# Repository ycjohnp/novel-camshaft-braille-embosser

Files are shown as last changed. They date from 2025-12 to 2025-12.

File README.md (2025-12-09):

# A Quieter and More Efficient Camshaft-Powered Braille Embosser 

**Introduction:**\
This project explores a camshaft-based approach to enhance braille embossers, addressing the challenges faced by visually impaired individuals. Traditional braille embossers are costly and noisy, hindering personal use. The proposed solution employs a camshaft system to improve efficiency, reduce noise, and lower costs. Unlike commercial alternatives ($2000-$5000) that require sound dampening, this camshaft-powered embosser operates quietly and is economically accessible at around 1000 RMB (approximately $160). The experiments conducted demonstrate the viability of this design, showcasing its potential as an affordable and effective braille embossing solution.

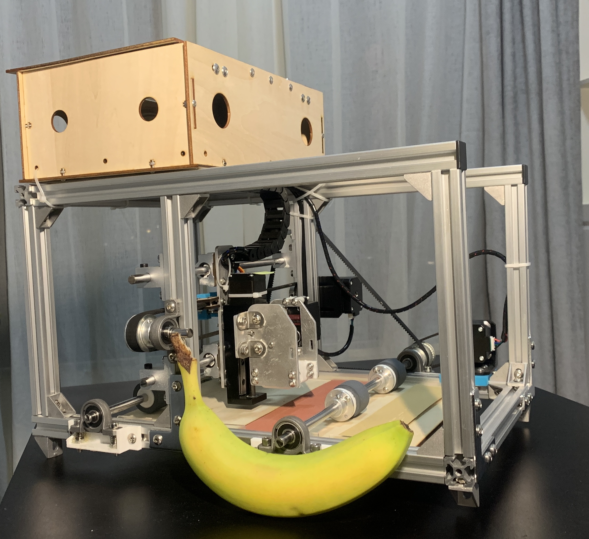
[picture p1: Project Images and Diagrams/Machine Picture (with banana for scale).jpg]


## Background

There are an estimated 43 million blind individuals worldwide, 233 million that are living with moderate to severe visual impairment.Visually impaired individuals rely on the use of braille letters instead of alphanumeric letters to write and read. Braille Characters are composed of a 2*3 grid of raised dots to form characters and can be generated through refreshable braille displays, manual braille writing slates, or braille embossers. Braille embossers are used to produce large amount of permanent braille characters.

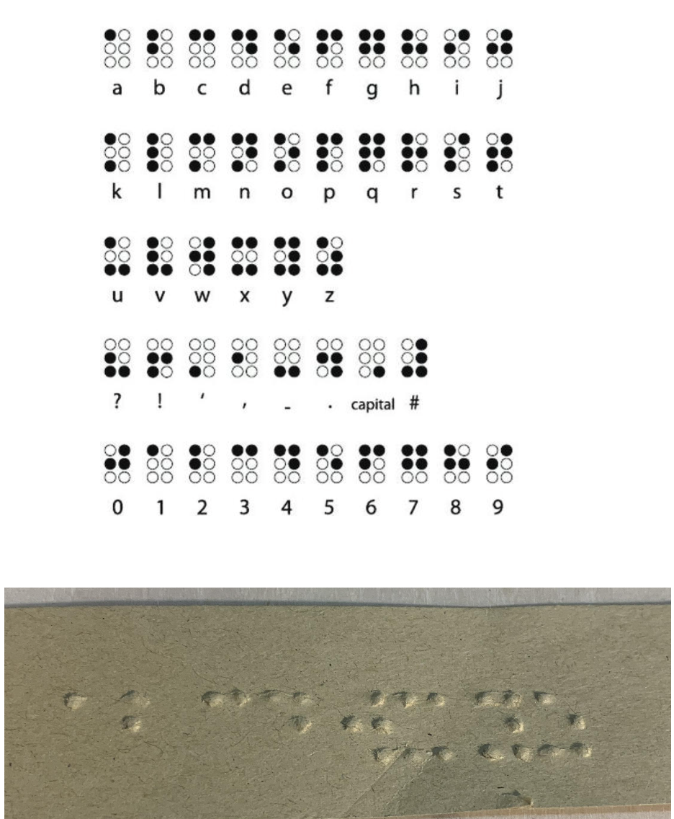
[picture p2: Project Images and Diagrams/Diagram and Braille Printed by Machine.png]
\
Diagram of braille characters and sample printed text from machine[^1].

Only 10% of blind individuals in the United States are proficient in braille. [^2] Commercial braille embossers, priced between $2000 and $5000, are impractical for personal use, mostly confined to schools and libraries. The widespread availability of such facilities has been limited, especially during the global pandemic. Currently, common commercial machines utilize loud linear solenoids, often necessitating sound dampening boxes. There is an absence of an efficient and quiet braille embosser suitable for home use in the current landscape.

**Engineering Goals:**\
Goal: Develop a highly efficient and low-noise braille embosser.
Design Criteria:
- Utilize off-the-shelf components.
- Generate braille following recognized standards.
- Enable simultaneous printing of multiple dots with scalability.
- Maintain operation noise below 60 dB.
- At a size for easy portability.
## Engineering Design

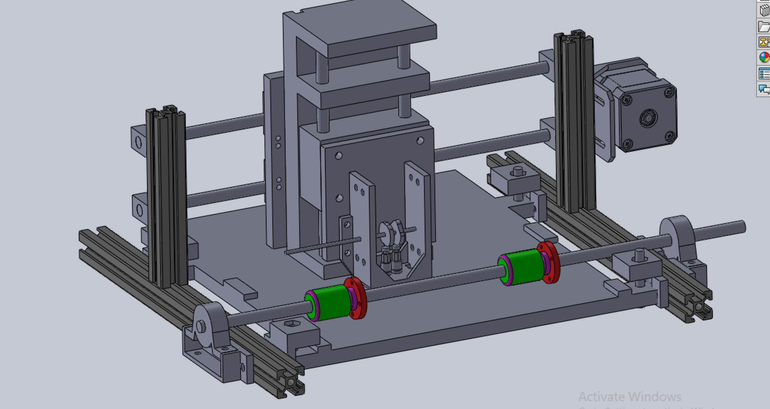
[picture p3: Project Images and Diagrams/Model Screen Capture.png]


This machine is based on a 3 axis motion system. 
In the diagram below: 
- The X axis is the belted linear motion system moves the printhead left and right on the as the machine is printing
- The Y axis is comprised of a system of rollers, that first feeds paper in, slides the paper up as each line of braille dots finishes printing, and releases the paper
- The Z axis is responsible for the up-down movement of the printhead. The lead-screw linear motion platform, pushes the printhead (and the print pins) into the paper, allowing for the dots to take shape

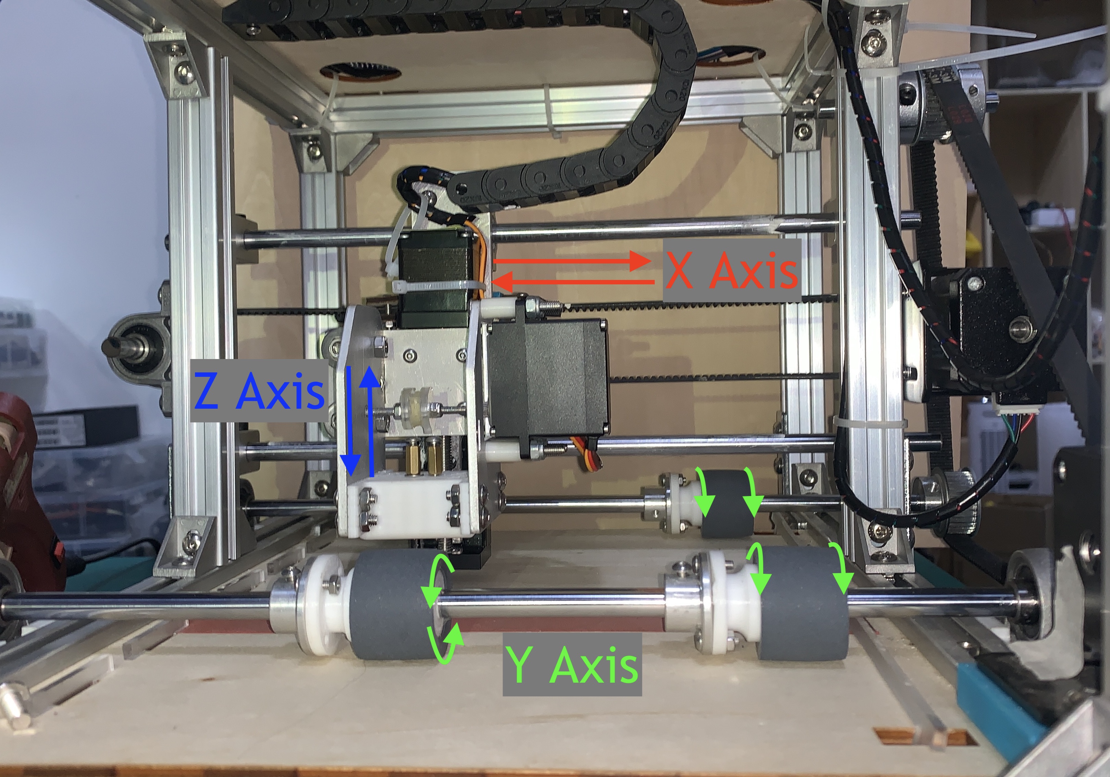
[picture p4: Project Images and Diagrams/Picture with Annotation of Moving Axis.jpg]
 

**Printhead Design:**

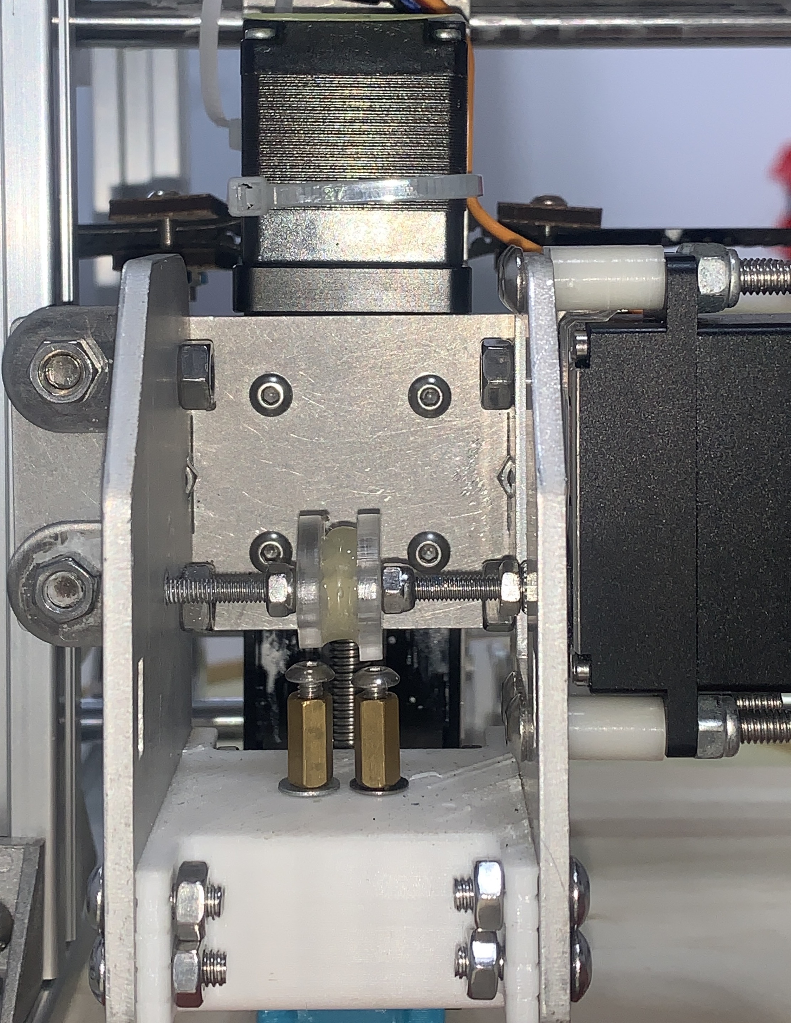
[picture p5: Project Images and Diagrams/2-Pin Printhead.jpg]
 

The main printhead assembly consists of a 360 degree servo that is a connected to a camshaft. This cam shaft has 2 cams on it and the cams have all the possible positions so that the print pins can pin all the possible combinations of "dot" and "no-dot". Underneath the cams are 2 print pins that are responsible for pushing the dots into the paper. These print pins are directly under the cams.

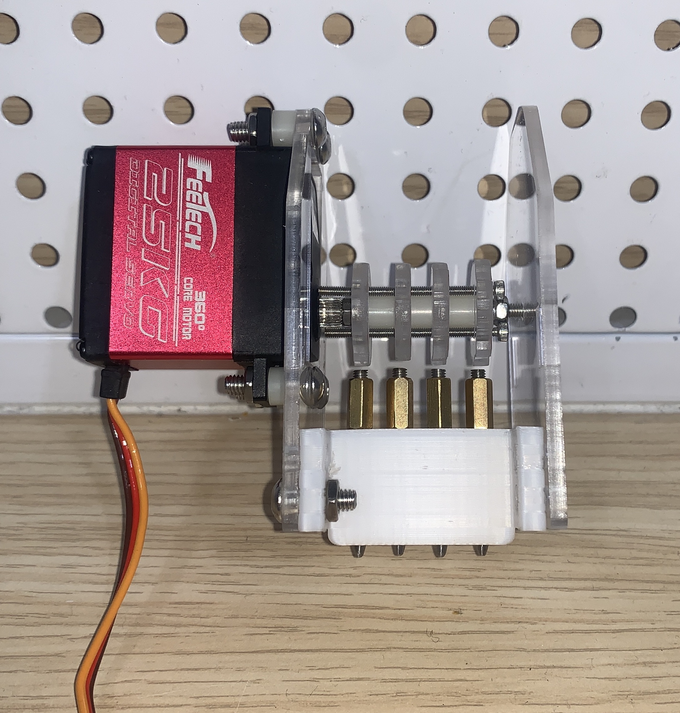
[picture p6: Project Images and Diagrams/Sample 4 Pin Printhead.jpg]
 

This 4 pin demo printhead shows theoretical maximum number of pins-per-printhead while maintaining accuracy when adjusting the positions of the cams. The protruding print pins are shown below.

## Testing

Several tests were conducted to verify the overall effectiveness of the printed braille. 

**Braille Dot Height Testing:**\
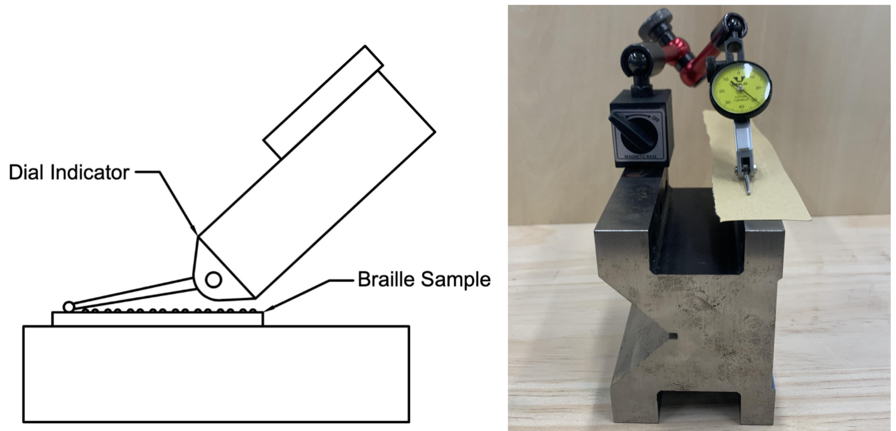
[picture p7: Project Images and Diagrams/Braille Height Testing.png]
 

From testing 5 different samples of the printed braille dots (characters: "abcdwxyz"), the average dot height was measured to be 0.32mm with a tolerance of ±0.12mm.

**Braille Dot Durability Testing:**

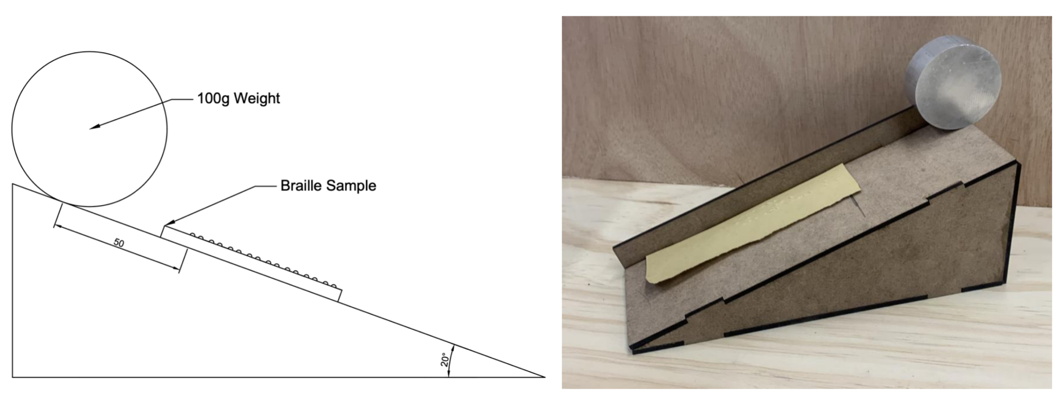
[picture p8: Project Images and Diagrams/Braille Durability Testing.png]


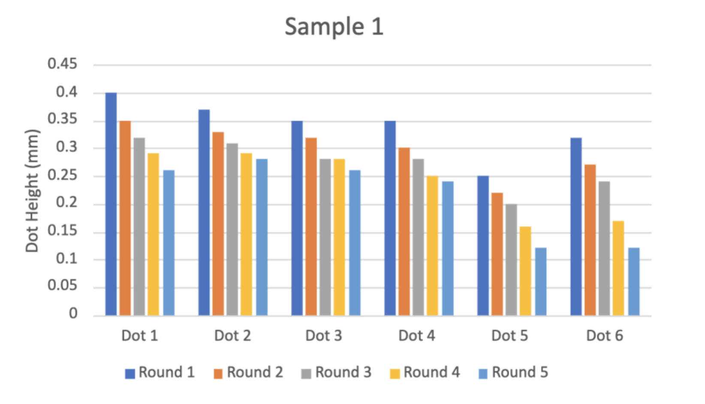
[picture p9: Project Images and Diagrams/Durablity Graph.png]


After 4 trials of durability testing, the average height loss for each dot was around 0.028mm.

## Conclusions

This project has showcased the feasibility of a low-cost,  efficient braille embosser employing a camshaft-based design. The printing mechanism has demonstrated success in generating braille dots and can be readily scaled to accommodate higher quantities. Future will be made particularly in areas such as exploring alternative manufacturing methods for print pins, elevating printer speed, and further scaling up the print head to accommodate even greater numbers of braille dots simultaneously. 
## Demo

Modular Robot Demo (https://www.youtube.com/watch?v=bNRHV4BrbQY&ab "Modular Robot Demo")

## Image Sources

[^1]: Self taken image of printed braille + Diagram from:\
Kumari, S., Akole, A., Angnani, P., Bhamare, Y., & Naikwadi, Z. (2020). Enhanced Braille display Use of OCR and Solenoid to improve text to braille conversion. 2020 International Conference for Emerging Technology (INCET). https://doi.org/10.1109/incet49848.2020.9153996

[^2]: Mates, B. T., & Reed, W. R. (2011). Assistive technologies in the library. American Library Association

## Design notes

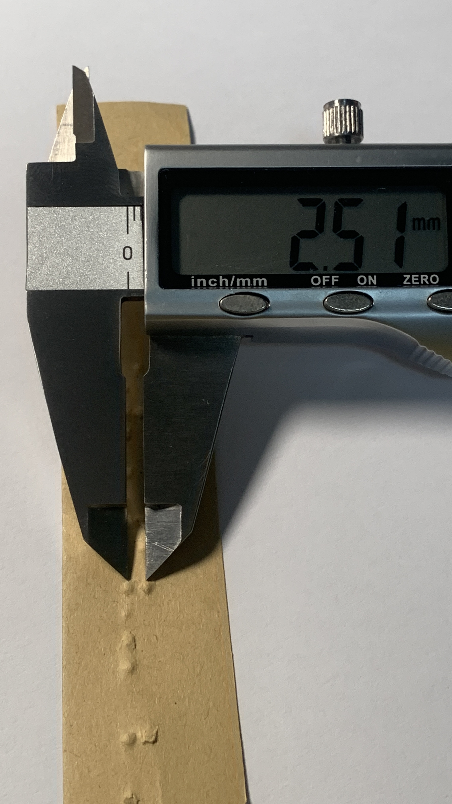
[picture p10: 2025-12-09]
Project Images and Diagrams/Braille Dot Vertical Spacing QC.jpg

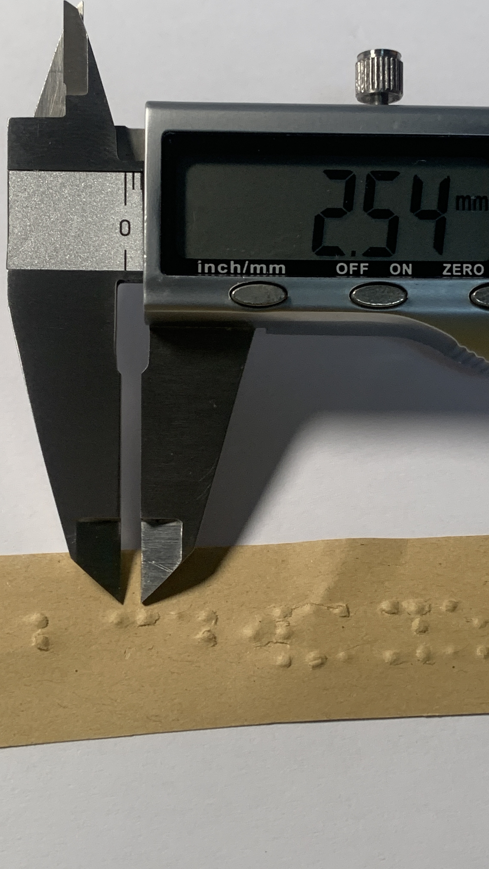
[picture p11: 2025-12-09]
Project Images and Diagrams/Braille Dot Horizontal Spacing QC.jpg

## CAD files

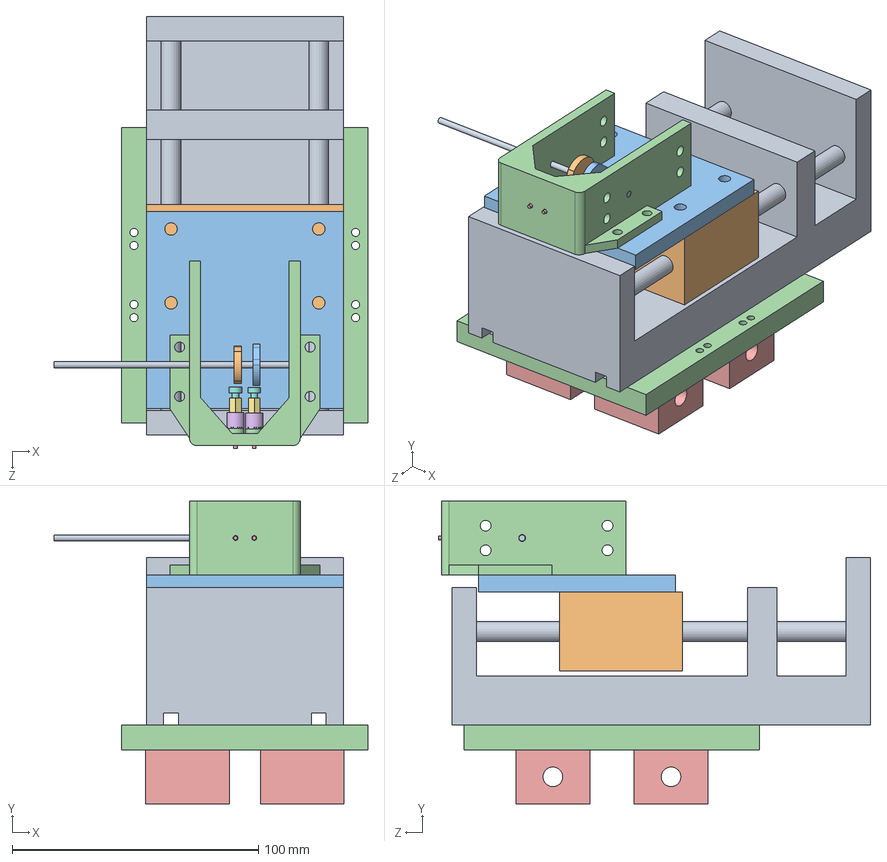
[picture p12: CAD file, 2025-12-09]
CAD Files/Fully Assembled Machine.SLDASM
127.5 x 123.0 x 175.5 mm
Main frame of smooth rod and bearing
Bearing block of the z axis
Print Head to Z adapter
Print Head Outershell
Printer Head Pins x 2
Print Head Adapter x 2
Brass Standoff in Print Head x 2
Screw In Printhead x 2
Axle
Gear 1 Print Head
Gear 2 Print Head
Linear Bearings to Z axis
Lienar Bearing Blocks x 4

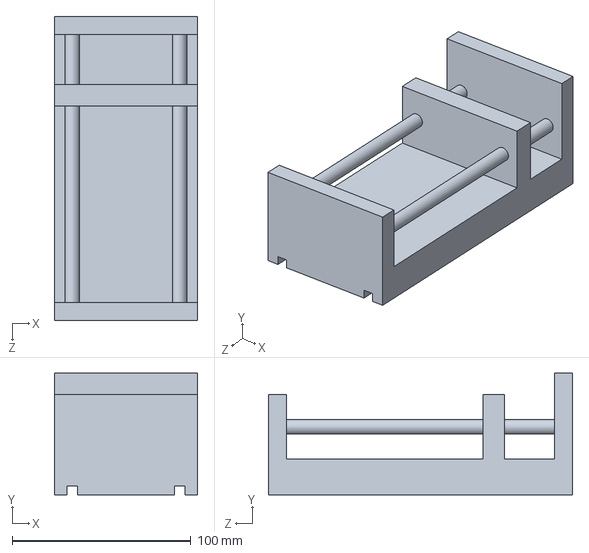
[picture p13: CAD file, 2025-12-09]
CAD Files/Z axis/Main frame of smooth rod and bearing.SLDPRT
80.0 x 68.0 x 170.0 mm

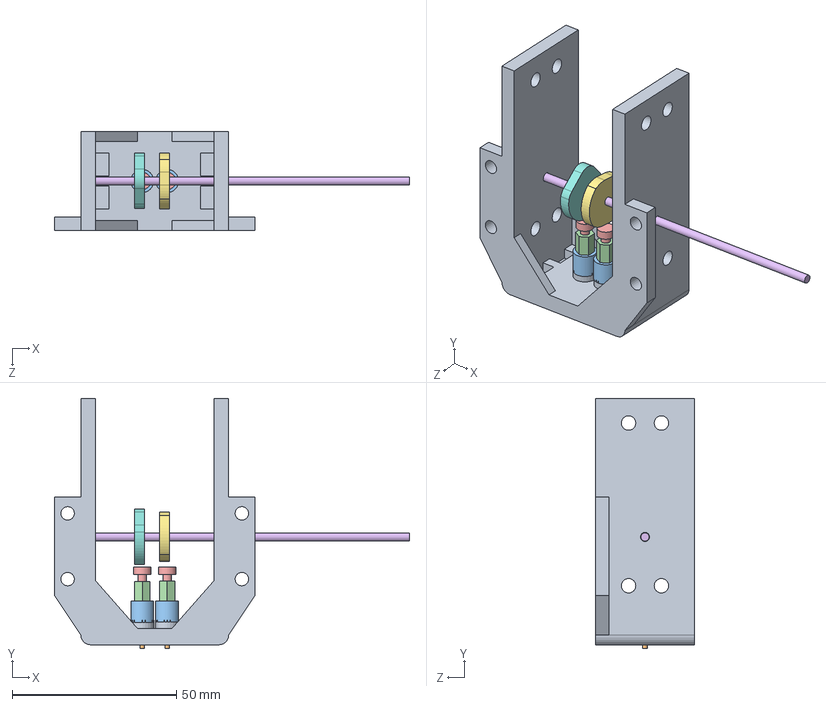
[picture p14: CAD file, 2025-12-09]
CAD Files/Print Head/Print Head Assembly.SLDASM
108.0 x 76.2 x 30.0 mm
Print Head Outershell
Printer Head Pins x 2
Print Head Adapter x 2
Brass Standoff in Print Head x 2
Screw In Printhead x 2
Axle
Gear 1 Print Head
Gear 2 Print Head

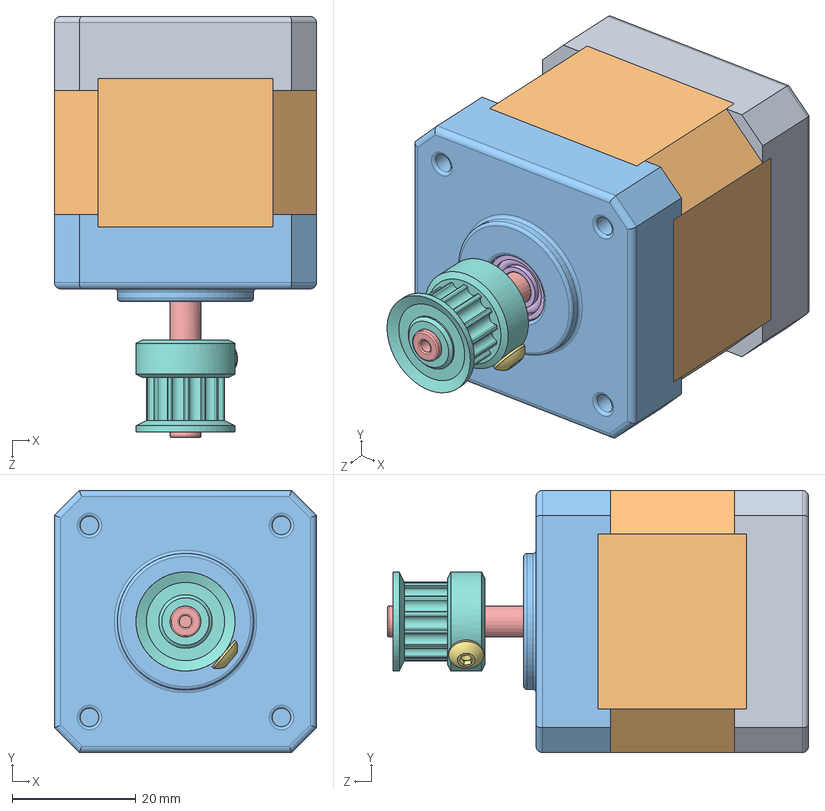
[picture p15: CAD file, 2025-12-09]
CAD Files/X-Axis Linear Motion/NEMA 17 with T5 Pulley.SLDASM
42.3 x 42.3 x 68.0 mm
Base
Cuerpo
Tapa
pan cross head_am_B18.6.7M - M3 x 0.5 x 5 Type I Cross Recessed PHMS --5N x 4
Eje
instrument ball bearing_68_am_AFBMA 12.1.4.1 - 0050-11 - 10,SI,NC,10_68 x 2
socket button head cap screw_am_B18.3.4M - 3 x 0.5 x 5 SBHCS --N
T5 Pulley

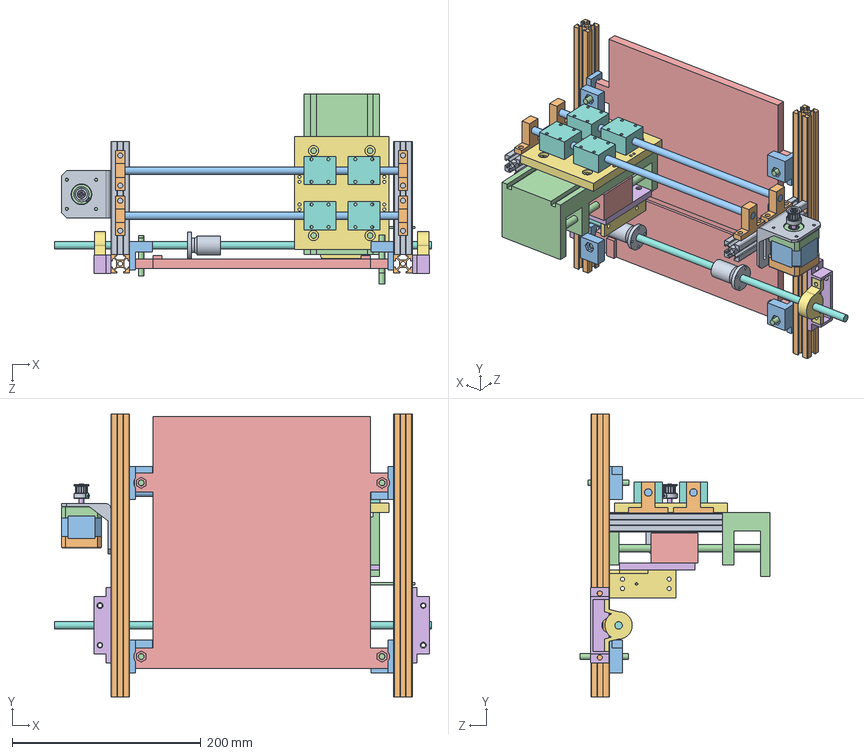
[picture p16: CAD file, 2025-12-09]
CAD Files/X-Axis Linear Motion/Assembly of X Z with 2020 V2.SLDASM
400.0 x 300.0 x 201.2 mm
2020 alu section v1 300 x 2
Smooth Rod to 2020 Extrusion x 4
smooth rod x 2
Main frame of smooth rod and bearing
Bearing block of the z axis
Print Head to Z adapter
Print Head Outershell
Printer Head Pins x 2
Print Head Adapter x 2
Brass Standoff in Print Head x 2
Screw In Printhead x 2
Axle
Gear 1 Print Head
Gear 2 Print Head
Linear Bearings to Z axis
Lienar Bearing Blocks x 4
NEMA_17_Bracket
Base
Cuerpo
Tapa
pan cross head_am_B18.6.7M - M3 x 0.5 x 5 Type I Cross Recessed PHMS --5N x 4
Eje
instrument ball bearing_68_am_AFBMA 12.1.4.1 - 0050-11 - 10,SI,NC,10_68 x 2
socket button head cap screw_am_B18.3.4M - 3 x 0.5 x 5 SBHCS --N
T5 Pulley
y axis bottom extrusion x 2
2020 to Printplate adaptor x 4
M6 screw x 4
Print plate
Y axis adjustment base x 2
zhouchenzuo V2 x 2
Y axis rod v2 8mm
y axis wheel adaptor x 2

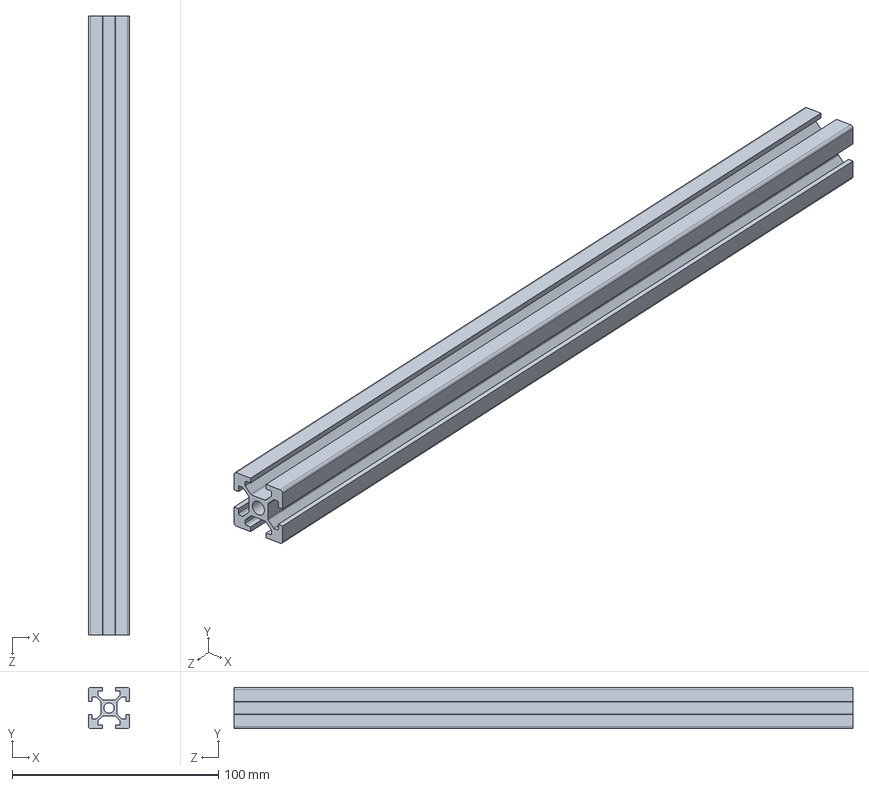
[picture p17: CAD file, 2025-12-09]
CAD Files/2020 alu section v1.SLDPRT
20.0 x 20.0 x 300.0 mm

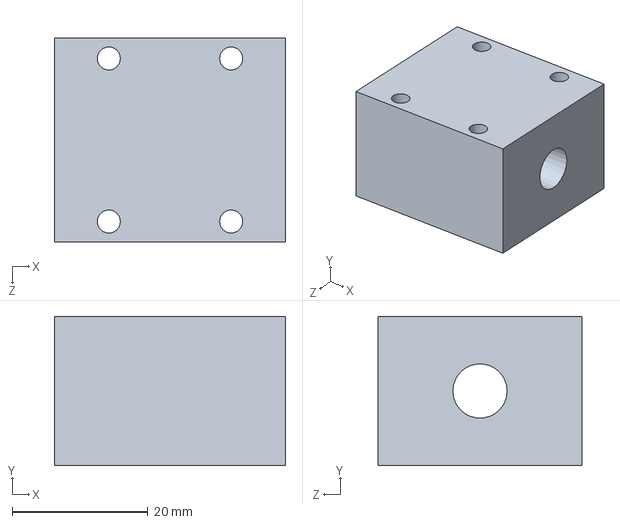
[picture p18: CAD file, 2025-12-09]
CAD Files/X-Axis Linear Motion/Linear Bearing Blocks.SLDPRT
34.0 x 22.0 x 30.0 mm

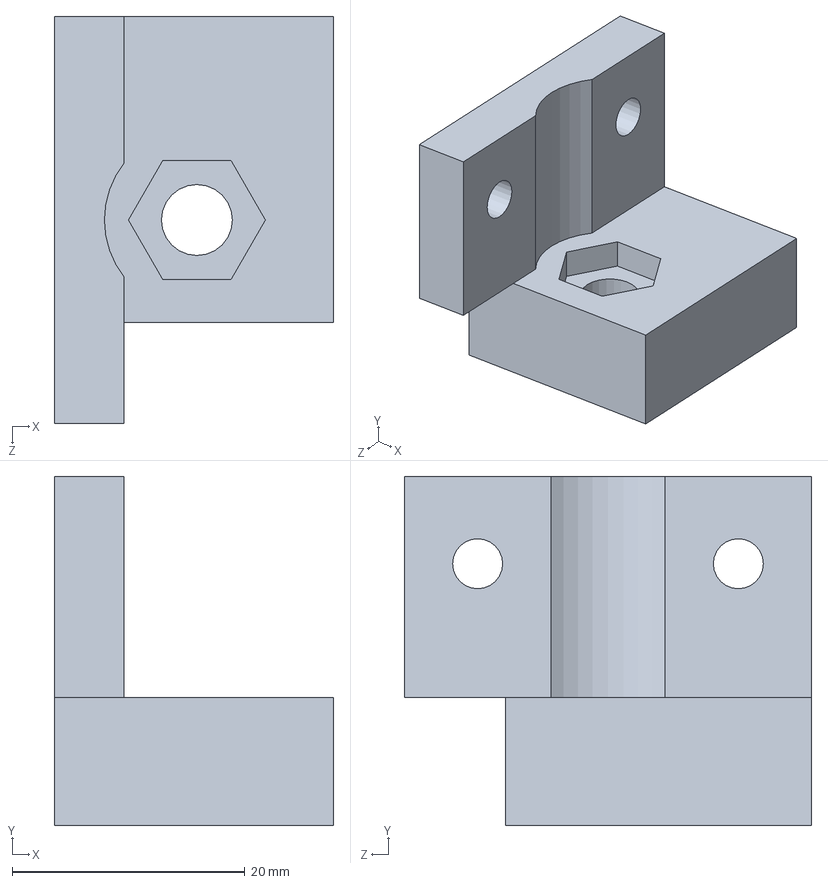
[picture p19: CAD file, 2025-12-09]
CAD Files/Y axis + frame/2020 to Printplate adaptor.SLDPRT
24.0 x 30.0 x 35.0 mm

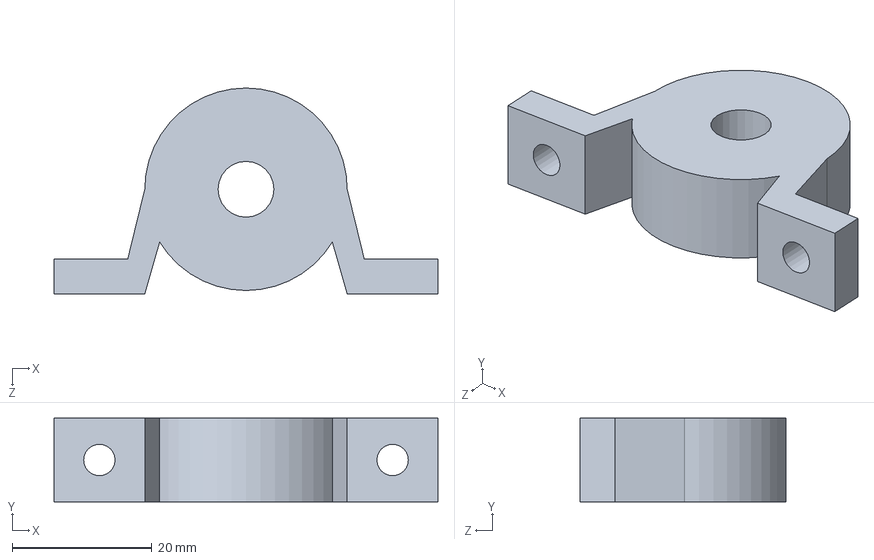
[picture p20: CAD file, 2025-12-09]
CAD Files/Y axis V2/zhouchenzuo V2.SLDPRT
55.0 x 12.0 x 29.5 mm

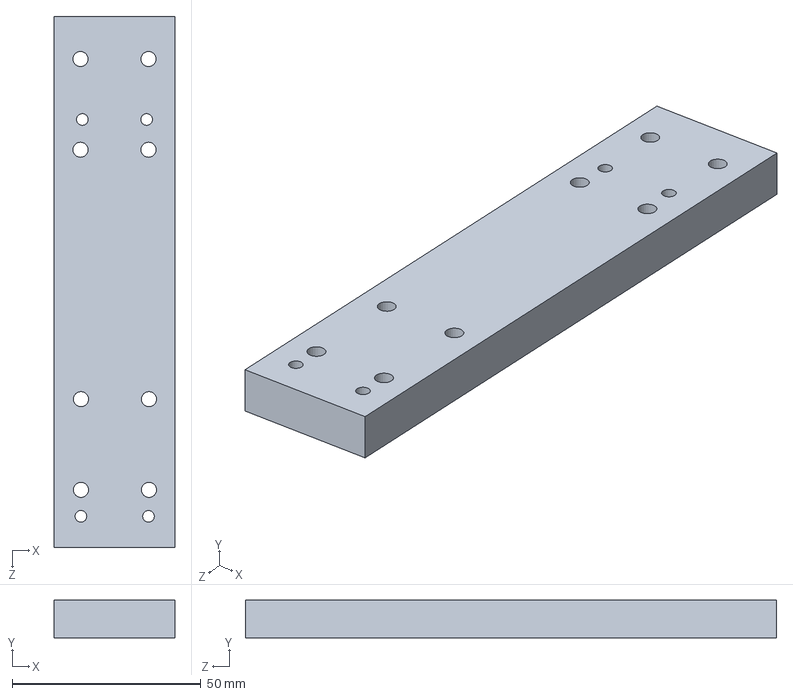
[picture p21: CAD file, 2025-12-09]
CAD Files/Z axis/Linear Bearing to Z axis V3.SLDPRT
32.0 x 10.0 x 140.5 mm

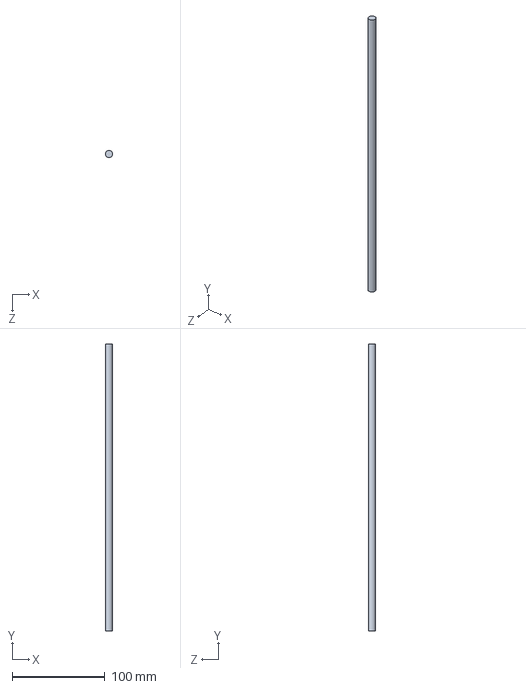
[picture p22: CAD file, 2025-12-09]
CAD Files/X-Axis Linear Motion/smooth rod.SLDPRT
8.00 x 310.0 x 8.00 mm

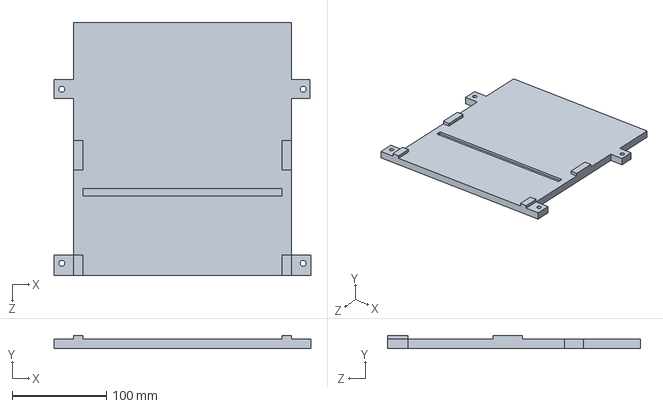
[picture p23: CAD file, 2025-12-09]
CAD Files/Y axis + frame/Print plate.SLDPRT
272.0 x 14.0 x 267.6 mm

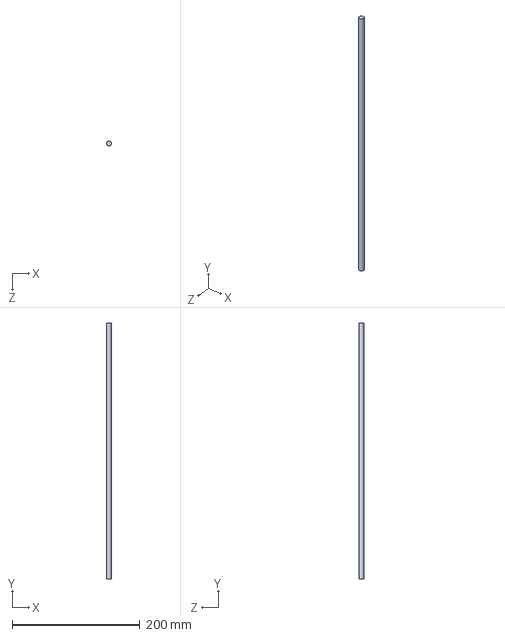
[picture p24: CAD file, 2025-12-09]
CAD Files/Y axis V2/Y axis rod v2 8mm.SLDPRT
8.00 x 400.0 x 8.00 mm

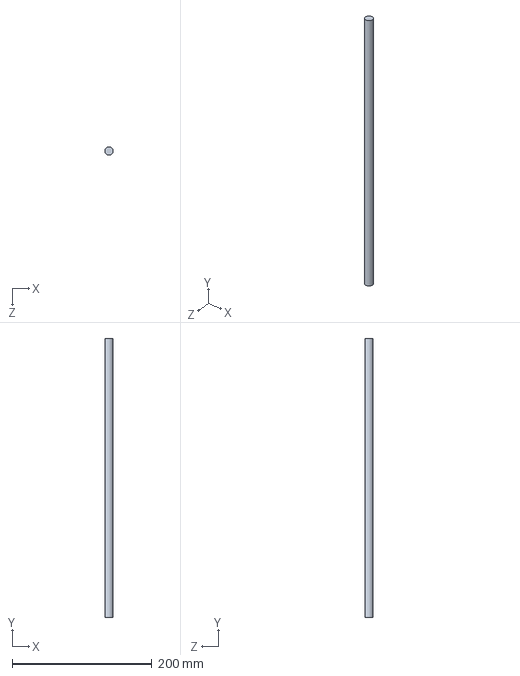
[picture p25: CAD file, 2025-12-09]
CAD Files/Y axis + frame/y axis rod.SLDPRT
12.0 x 400.0 x 12.0 mm

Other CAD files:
CAD Files/Print Head/Print head gear wheels 0101 V2.DWG.SLDPRT
CAD Files/Print Head/Print head gear wheels 0011 V2.SLDPRT
CAD Files/Y axis V2/y axis wheel adaptor.SLDPRT
CAD Files/Z axis/Print head to Z asix.SLDPRT
CAD Files/Print Head/3.5mm 6mm.SLDPRT
CAD Files/Print Head/3.5mm 7mm.SLDPRT
CAD Files/Print Head/Axle.SLDPRT
CAD Files/Print Head/Brass Standoff in Print Head.SLDPRT
CAD Files/Print Head/Gear 1 Print Head.SLDPRT
CAD Files/Print Head/Gear 2 Print Head.SLDPRT
CAD Files/Print Head/Print Head Adapter.SLDPRT
CAD Files/Print Head/Print Head Cam Designs.dwg
CAD Files/Print Head/Print Head Frame.dwg
CAD Files/Print Head/Print Head Outershell.SLDPRT
CAD Files/Print Head/Printer Head Pins.SLDPRT
CAD Files/Print Head/Screw In Printhead.SLDPRT
CAD Files/X-Axis Linear Motion/2020 alu section v1 300.SLDPRT
CAD Files/X-Axis Linear Motion/2020 alu section.SLDPRT
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

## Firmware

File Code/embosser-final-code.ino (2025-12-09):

#include <SoftwareSerial.h>
#include <Servo.h>
//SoftwareSerial Braille_Printer(12,13);
Servo myservo;
#define servoPin 7
#define zdirPin 13
#define zstepPin 12
#define down 0
#define up 1
#define left 1
#define right 0
#define xdirPin 5
#define xstepPin 6
#define ydirPin 8
#define ystepPin 9
int printfinished = 0;
int start = 1;
int ydistance = 20; //33 esteps/mm this is at 1/16 microstepping
int xdistance = 220; // 20 esteps/mm this is at 1/32 microstepping
float zdistance = 5.7; // 100 esteps/mm
float xtraveleddistance = 0;
int speed_stepprt = 400;
int num1, num2, j, length, totle, updig_sum = 0, updig_sum_last = 0, printcode;
String row[10];
String line[3], code[2];
String alphabet[31][3][2] = {
  {{"1", "0"}, {"0", "0"}, {"0", "0"}}, //a
  {{"1", "0"}, {"1", "0"}, {"0", "0"}}, //b
  {{"1", "1"}, {"0", "0"}, {"0", "0"}}, //c
  {{"1", "1"}, {"0", "1"}, {"0", "0"}}, //d
  {{"1", "0"}, {"0", "1"}, {"0", "0"}}, //e
  {{"1", "1"}, {"1", "0"}, {"0", "0"}}, //f
  {{"1", "1"}, {"1", "1"}, {"0", "0"}}, //g
  {{"1", "0"}, {"1", "1"}, {"0", "0"}}, //h
  {{"0", "1"}, {"1", "0"}, {"0", "0"}}, //i
  {{"0", "1"}, {"1", "1"}, {"0", "0"}}, //j
  {{"1", "0"}, {"0", "0"}, {"1", "0"}}, //k
  {{"1", "1"}, {"1", "0"}, {"1", "0"}}, //l
  {{"1", "1"}, {"0", "0"}, {"1", "0"}}, //m
  {{"1", "1"}, {"0", "1"}, {"1", "0"}}, //n
  {{"1", "0"}, {"0", "1"}, {"1", "0"}}, //o
  {{"1", "1"}, {"0", "0"}, {"0", "0"}}, //p
  {{"1", "1"}, {"1", "1"}, {"1", "0"}}, //q
  {{"1", "0"}, {"1", "1"}, {"1", "0"}}, //r
  {{"0", "1"}, {"1", "0"}, {"1", "0"}}, //s
  {{"0", "1"}, {"1", "1"}, {"1", "0"}}, //t
  {{"1", "0"}, {"0", "0"}, {"1", "1"}}, //u
  {{"1", "0"}, {"1", "0"}, {"1", "1"}}, //v
  {{"0", "1"}, {"1", "1"}, {"0", "1"}}, //w
  {{"1", "1"}, {"0", "0"}, {"1", "1"}}, //x
  {{"1", "1"}, {"0", "1"}, {"1", "1"}}, //y
  {{"1", "0"}, {"0", "1"}, {"1", "1"}}, //z
  {{"0", "1"}, {"0", "1"}, {"1", "1"}}, // hastag
  {{"0", "0"}, {"0", "0"}, {"0", "1"}}, // capitalization symbol
  {{"0", "0"}, {"0", "0"}, {"0", "0"}}, //empty
  {{"0", "0"}, {"1", "0"}, {"0", "0"}}, //,
  {{"0", "0"}, {"1", "1"}, {"0", "1"}} //.

};
//170  01   0
//30   10   50
//80   11   100
//130  00   160

void setup() {
  // put your setup code here, to run once:
  Serial.begin(9600);
  //  Braille_Printer.begin(9600);
  pinMode(zstepPin, OUTPUT);
  pinMode(zdirPin, OUTPUT);
  pinMode(xstepPin, OUTPUT);
  pinMode(xdirPin, OUTPUT);
  pinMode(ystepPin, OUTPUT);
  pinMode(ydirPin, OUTPUT);
  digitalWrite(zdirPin, HIGH);
  myservo.attach(servoPin);
  code[0] = code[1] = "";
  ymove(200, down); delay (1000);
  zmove(19, down); delay (1000);

}

void loop() {

  myservo.write(160);
  
  if (Serial.available())
  {
    String str = Serial.readString();
    length = str.length();
    //if(length>0)      printfinished ==1;
    for (int k = 0; k < str.length(); k++)
    {
      if (isupper(str[k]))
        length++;
      if (isdigit(str[k]))
        length++;
    }

    for ( j = 0; j < length / 20 + 1; j++)
    {
      totle = 20;
      for (int k = j * 20 - updig_sum_last; k < j * 20 - updig_sum_last + totle; k++)
      {
        if (isupper(str[k]))
        {
          totle--; updig_sum++;
        }
        else if (isdigit(str[k]))
        {
          totle--; updig_sum++;
        }
        row[j] += str[ k];
        if (str[ k + 1] == '\0')  break;
      }
      updig_sum_last = updig_sum;
    }
    Serial.print("row[0]:"); Serial.println(row[0]);
    Serial.print("row[1]:"); Serial.println(row[1]);
    for (int m = 0; m < j; m++)
    {
      for (int i = 0; i < row[m].length(); i++)
      {
        if (row[m][i] == ' ')   num1 = 28;
        else if (isupper(row[m][i]))
        {

          line[0] = line[0] + alphabet[27][0][0] + alphabet[27][0][1];
          line[1] = line[1] + alphabet[27][1][0] + alphabet[27][1][1];
          line[2] = line[2] + alphabet[27][2][0] + alphabet[27][2][1];
          num1 = row[m][i] - 'A';
        }
        else if (isdigit(row[m][i]))
        {
          line[0] = line[0] + alphabet[26][0][0] + alphabet[26][0][1];
          line[1] = line[1] + alphabet[26][1][0] + alphabet[26][1][1];
          line[2] = line[2] + alphabet[26][2][0] + alphabet[26][2][1];
          num1 = row[m][i] - '0';
        }
        else if (islower(row[m][i]))
          num1 = row[m][i] - 'a';
        else if (row[m][i] == ',')
          num1 = 29;
        else if (row[m][i] == '.')
          num1 = 30;
        else  break;
        line[0] = line[0] + alphabet[num1][0][0] + alphabet[num1][0][1];
        line[1] = line[1] + alphabet[num1][1][0] + alphabet[num1][1][1];
        line[2] = line[2] + alphabet[num1][2][0] + alphabet[num1][2][1];
      }
      for (int c = 0; c < 3; c++)
        if (line[c].length() % 4 != 0)
          line[c] = line[c] + "0" + "0";
      Serial.print("line[0]:"); Serial.println(line[0]);
      Serial.print("line[1]:"); Serial.println(line[1]);
      Serial.print("line[2]:"); Serial.println(line[2]);
      for (int n = 0; n < 3; n++)
      {

        for (int p = line[n].length() - 1; p >= 0; p--)
        {
          //Serial.print("line[n].length():");Serial.println(line[n].length());
          if (((p + 1) % 4 == 0) && line[n][p - 3] != '\0')
          {
            code[0] = code[0] + line[n][p] + line[n][p - 2];
            code[1] = code[1] + line[n][p - 1] + line[n][p -  3];
            Serial.print("code[0]:"); Serial.println(code[0]);
            Serial.print("code[1]:"); Serial.println(code[1]);
          }
          if (code[0] != "")
          {
            //Serial.print("code[0]:");Serial.println(code[0]);
            //Serial.print("code[1]:");Serial.println(code[1]);
            printcode = code[0].toInt();
            print_code(printcode);
            xmove(3.5, right, 800); //11.5
            printcode = code[1].toInt();
            print_code(printcode);
            xmove(12.55, right, 600);//18.7
            xtraveleddistance += 16.05;//28/2
            Serial.print("xtraveleddistance:");
            Serial.println(xtraveleddistance);
          }
          code[0] = code[1] = "";
        }

        ymove(4, down);
        Serial.print("xtraveleddistance:");
        Serial.println(xtraveleddistance);
        xmove(xtraveleddistance, left, 400);
        xtraveleddistance = 0;
        delay(2000);
      }
      ymove(2.5, down);
      line[0] = line[1] = line[2] = "";
    }
    printfinished == 1;
    Serial.print("printfinished") ;
    ymove(400, down);
    zmove(27, up);
  }
  if (printfinished == 1) {
    Serial.print("printfinished") ;
    ymove(400, down);
    zmove(27, up);
  }

}
void print_code(int code) {
  switch (code) {
    case 00: myservo.write(140); delay(2000); zmove(zdistance, down); delay(800); zmove(zdistance, up); zmove(zdistance, down); delay(800); zmove(zdistance, up); break;
    case 10: myservo.write(30); delay (2000); zmove(zdistance, down); delay(800); zmove(zdistance, up); zmove(zdistance, down); delay(800); zmove(zdistance, up); break;
    case 01: myservo.write(180); delay (2000); zmove(zdistance, down); delay(800); zmove(zdistance, up); zmove(zdistance, down); delay(800); zmove(zdistance, up); break;
    case 11: myservo.write(90); delay (2000); zmove(zdistance, down); delay(800); zmove(zdistance, up); zmove(zdistance, down); delay(800); zmove(zdistance, up); break;
  }
}

void zmove(float mm, int direct) {
  int steps = 100 * mm;
  digitalWrite(zdirPin, direct);
  for (int i = 0; i < steps; i++)
  {
    digitalWrite(zstepPin, HIGH);
    delayMicroseconds(speed_stepprt);
    digitalWrite(zstepPin, LOW);
    delayMicroseconds(speed_stepprt);
  }
}

void xmove(float mm, int direct, int speed) {
  int steps = mm * 76;
  digitalWrite(xdirPin, direct);
  for (int i = 0; i < steps; i++)
  {
    digitalWrite(xstepPin, HIGH);
    delayMicroseconds(speed);
    digitalWrite(xstepPin, LOW);
    delayMicroseconds(speed);
  }
}

void ymove(float mm, int direct) {
  int steps = mm * 33;
  digitalWrite(ydirPin, direct);
  for (int i = 0; i < steps; i++)
  {
    digitalWrite(ystepPin, HIGH);
    delayMicroseconds(speed_stepprt);
    digitalWrite(ystepPin, LOW);
    delayMicroseconds(speed_stepprt);
  }
}
